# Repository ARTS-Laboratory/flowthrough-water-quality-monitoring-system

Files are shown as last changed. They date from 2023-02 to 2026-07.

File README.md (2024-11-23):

# Flowthrough Water Quality Monitoring System

This system monitors water quality by measuring conductivity, pH, and temperature, ensuring continuous operation with minimal maintenance. Moreover, versions of this system enable the use of time-domain nuclear magnetic resonance to be performed in situ. It features a robust construction that protects electrical components from environmental damage, supports an adequate flow rate for in situ water sampling, and enables data transmission to a server for analysis.

<p align="center">
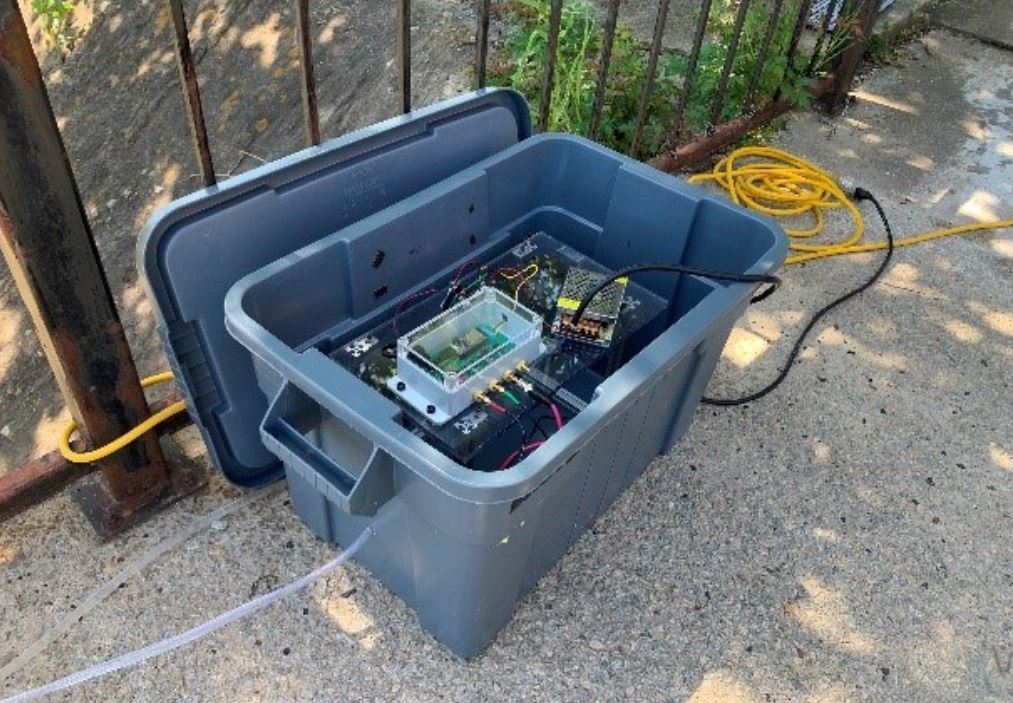
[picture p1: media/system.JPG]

</p>
<p align="center">
Figure 1: flow-through water quality monitoring deployed at USC to monitor water quality in the Rocky Branch in Columbia South Carolina.
</p>

## System Development
Contains the hardware and software developed for the project. 

## Licensing and Citation

This work is licensed under a Creative Commons Attribution-ShareAlike 4.0 International License [cc-by-sa 4.0].



Cite this as: 

@Misc{ARTSLabFlowthroughWaterQuality,    
  author = {ARTS-Lab},  
  howpublished = {GitHub},  
  title  = {Flowthrough Water Quality Monitoring System},   
  groups = {ARTS-Lab},    
  url    = {https://github.com/ARTS-Laboratory/flowthrough-water-quality-monitoring-system},   
}

<p align="center">
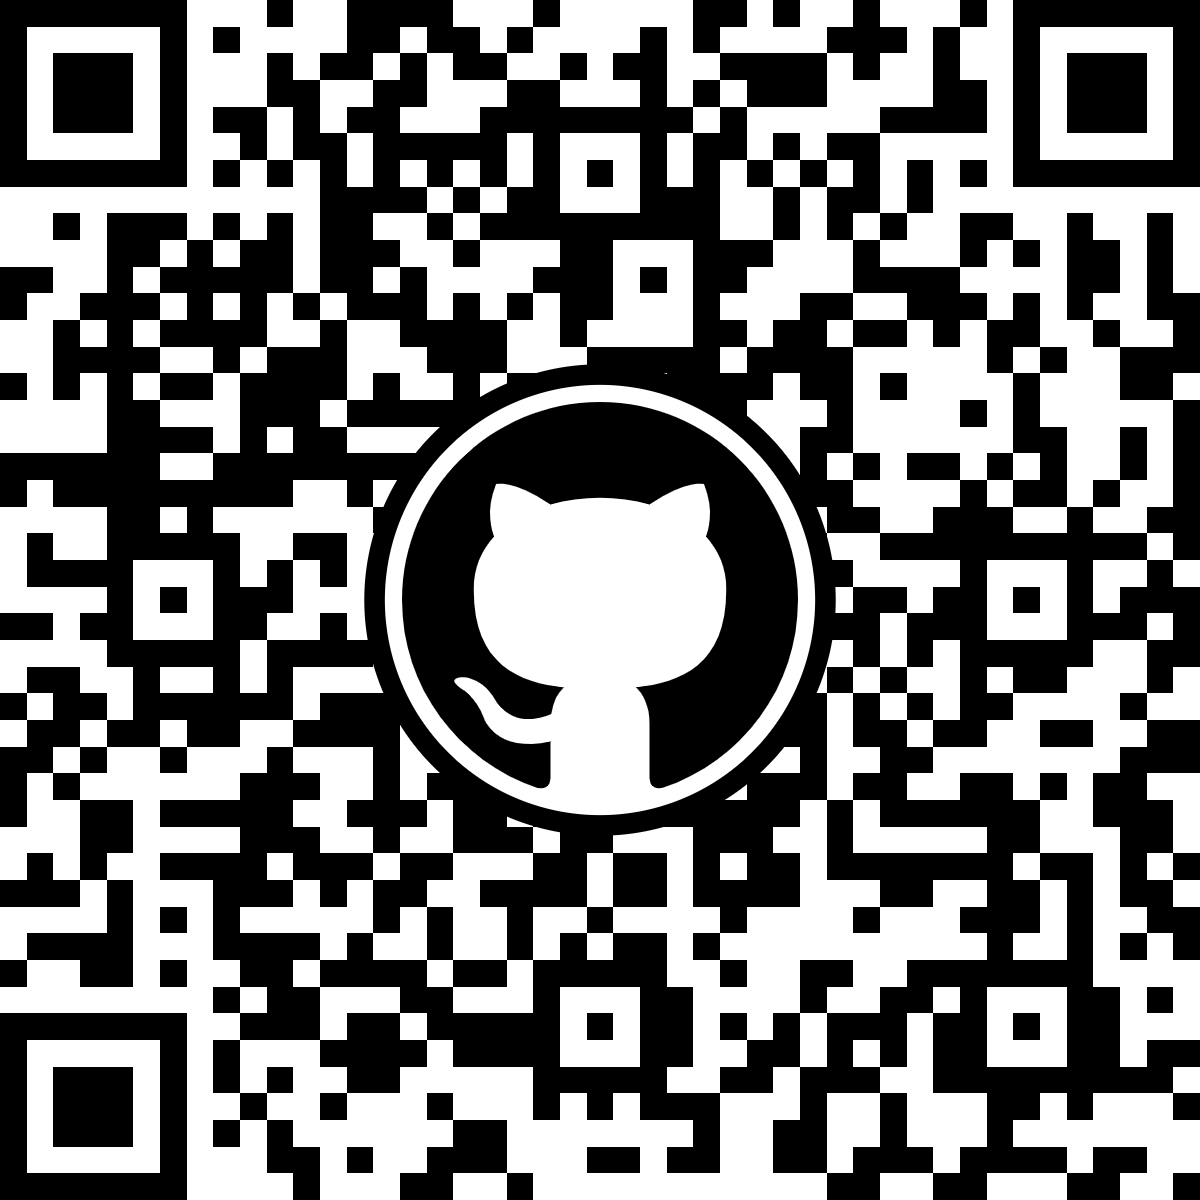
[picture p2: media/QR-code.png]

</p>
<p align="center">
QR code for repo.
</p>

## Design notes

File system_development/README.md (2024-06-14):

# System Development
Variations of the flow through the water quality system are being developed. Named after lakes in South Carolina 

## Keowee
A flow-through water quality monitoring system that measures PH, TDS, water temperature, and ambient temperature.

## Moultrie
A flow-through water quality monitoring system that integrates nuclear magnetic resonance monitoring and measures PH, TDS, water temperature, and ambient temperature.

## Marion
A prototype project beginning work in May of 2024 to combine a flowthrough NMR, a water quality, and a water height monitoring system.

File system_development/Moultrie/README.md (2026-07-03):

# Moultrie
A flow-through water quality monitoring system that integrated nuclear magnetic resonance monitoring as well as measuring PH, TDS, Water Temperature, and ambient Temperature.

## V0.1.0
An initial senior design project undertaken at USC that laid out initial system aspects. 

## V0.2.0
A senior Design projecc form teh spring-fall of 2025.

## V0.3.0 
A version further developed from the Senior Design project with simplified manufacturability and newer magnets.

## V0.3.1 
A cleaned up verion of V0.3.0 with the extra CAD files removed.

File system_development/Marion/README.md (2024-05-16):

#Files for use with the Prototype-24 project

##PCB Files
Kicad files as well as general information about the custom PCB's used with the water height monitoring and pumping system system.

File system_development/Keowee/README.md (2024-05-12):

# Keowee
A flow-through water quality monitoring system that measures PH, TDS, Water Temperature, and ambient Temperature.

## V0.1
1. An initial senior design project undertaken at USC that laid out initial system aspects. 

## V0.2
1. Measures PH, TDS, Water Temperature, and ambient Temperature.
2. Saves the Data collected on an SD card.
3. Using RTC to control and display the sampling time.
4. Using a relay to control the pumps.

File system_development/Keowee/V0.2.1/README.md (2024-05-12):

# V0.2
Measures PH, TDS, Water Temperature, and ambient Temperature and saves Saves the Data collected on an SD card.

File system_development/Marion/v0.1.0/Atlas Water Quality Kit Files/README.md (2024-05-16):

#Files for use with the Prototype-24 project and the Atlas Scientific Wifi Hydroponics 2.0 kit which we are using

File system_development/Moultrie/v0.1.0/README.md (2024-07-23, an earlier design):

# V0.1

Hello! Hopefully the work I did here was somewhat helpful. If you have questions about any of the physical structure or the Arduino relay system, please feel free to contact me at the following:

bmontroy25@governors.school (will work until the end of may, 2025)
braedenmontroy1@gmail.com (will always work)
228-382-8652 (quickest answer)

Hey, this is Ali. I continued to work on the water sensor array after Braeden left. If you have any questions about that array you can contact me at aliwallam16@gmail.com

# Pumps
The pumps we are using are 12V Grothen pumps. You'll need about 2 amps to run both of them at full power at the same time.
(https://www.amazon.com/dp/B0863TCH65)

# Relay
I've left a picture of the relay labelled in the same folder as this. It should have everything you need to get this going. Currently, the system works by powering the pumps whenever the D13 on the Arduino is on. As I was leaving, we were working on making this output a switch toggle.

<p align="center">
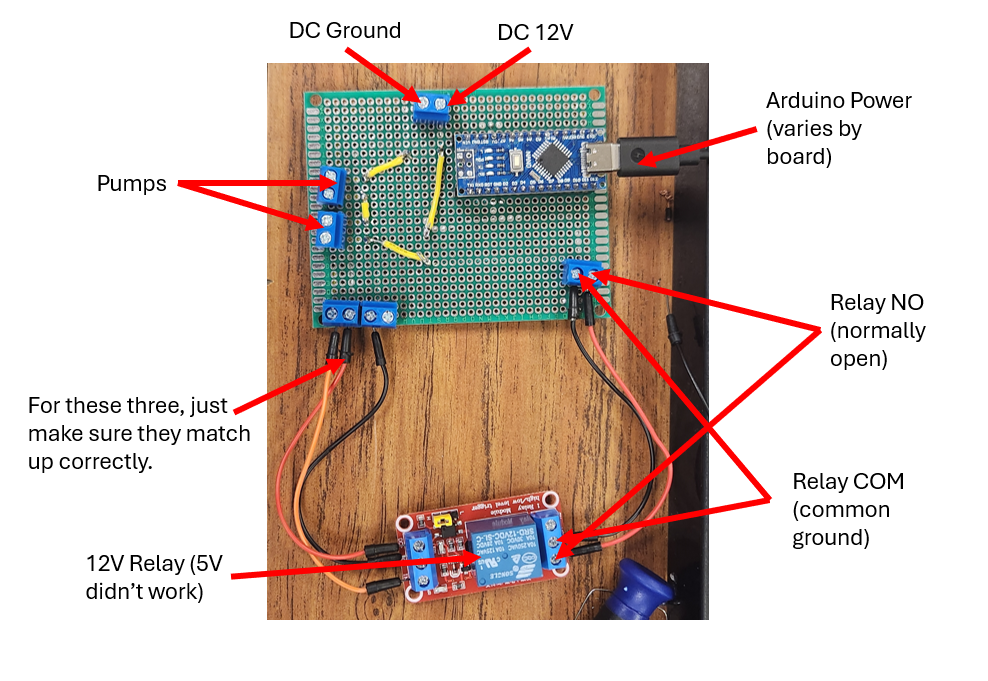
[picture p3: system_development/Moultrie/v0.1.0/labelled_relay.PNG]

</p>
<p align="center">

# Structure
The structure is currently made from 8020 and a sheet of what I think is Delrin. It doesn't fit in the box completely, as it needs about an inch to be chopped off the height in order to fit correctly, but all of the components fit inside of it. You can find CAD for this in the CAD folder in this directory. The next steps in terms of structure are to lower the right (or left) side to compensate for the PXIe, move all of the pumps to one side, use plastic screws and put the magnet on the other side, and make the connection between the pumps and the tubing and the sensor array watertight so water can actually run through the system.

# Water Sensor Array
Kit being used: https://atlas-scientific.com/kits/wi-fi-hydroponics-kit/

The array is now wired up to an SD card module as follows:
VCC (SD Card Module) to 3V (ESP32)
GND (SD Card Module) to GND (ESP32)
CS (SD Card Module) to GPIO 27 (ESP32)
MOSI (SD Card Module) to MOSI (ESP32)
MISO (SD Card Module) to MISO (ESP32)
SCK (SD Card Module) to SCK (ESP32)

The sensors themselves can take data and the code HFOIFHIOHFOIWHOW is set up to save the data to an sd card, they just need to be calibrated correctly to take data. The pH sensor currently connected to the array may not work together as it was not kept in the storage solution.

The kit is also connected to a TDS meter from keystudio: https://wiki.keyestudio.com/KS0429_keyestudio_TDS_Meter_V1.0

If you encounter issues they are likely power issues, in which case I would recommend adding a battery and a voltage regulator to the circuit.

<p align="center">
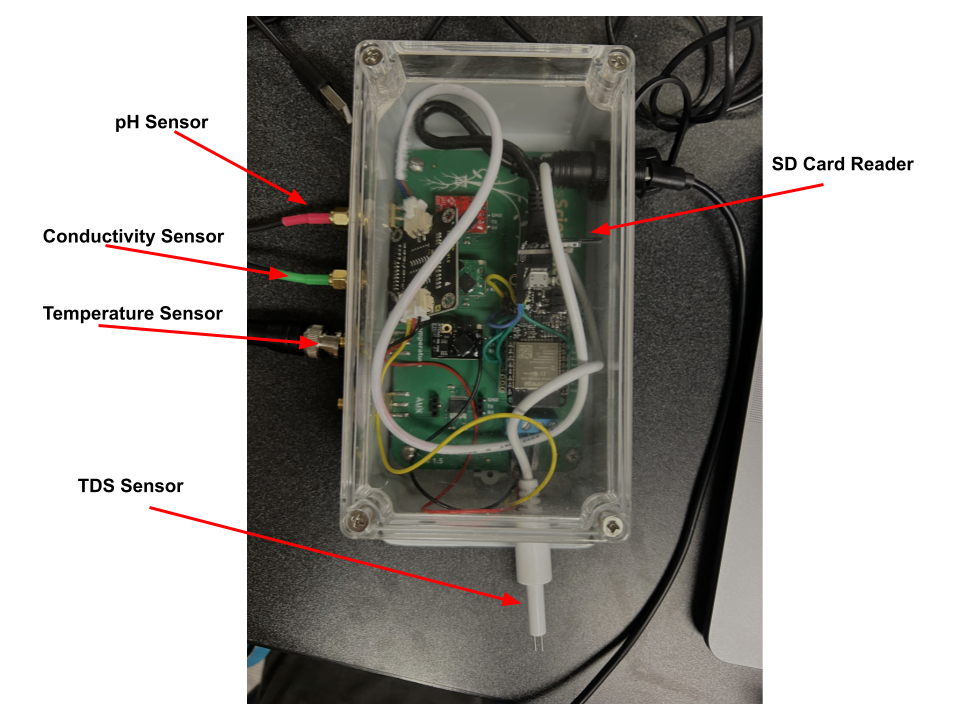
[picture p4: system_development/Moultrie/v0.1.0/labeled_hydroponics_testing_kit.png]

</p>
<p align="center">

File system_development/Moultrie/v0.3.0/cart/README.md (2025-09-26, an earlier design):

# Cart Design for the Moultrie V0.3
A fart for moving the flow-through water quality monitoring system that integrated nuclear magnetic resonance monitoring.

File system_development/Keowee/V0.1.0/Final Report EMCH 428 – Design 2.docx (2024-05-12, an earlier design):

In Situ Water Quality Measurement System

Abdullah Alghamdi, Carter hoyle, Michael Bertram, Grayson mobley

Final Report | EMCH 428 – Design 2

April 24, 2023

Department of Mechanical Engineering | University of South Carolina: Columbia, SC

Industry Sponsor: Dr. Austin Downey | The ARTS Laboratory

2. Table of Contents

Cover Page: 1

Table of Contents: 2

Executive Summary: 3-4

Background: 7

Customer Needs: 8-15

Project Specifications: 16-21

Functional Concepts: 22-31

Concept Selection: 33-35

Product Architecture: 36-39

Engineering Analysis: 40-50

Manufacturability: 51-56

Product Cost/ Economic Analysis: 58-62

Testing: 63-67

Final Design: 68

Conclusions: 69-71

Appendix: 72-73

3. Executive Summary

Dr. Austin Downey is a Professor at the University of South Carolina, and he oversees the Adaptive Real-Time Systems (ARTS) Laboratory that specializes in developing tools for systems that can adapt to the environment in real time. They want a product that does that can measure conductivity, pH, and temperature of water, provide adequate flow for fresh sampling, keep electrical components safe from water damage/heating damage, and will be able to transmit data to a server so they can have a device that can be compatible with the NMR.

The needs of Dr. Downey were determined by the project scope which gives a description of what the project entails and its deliverables, and the various project meetings that were held with the project sponsor, and after detailed analysis, it was determined that having sensors that can measure pH, measure conductivity, measure temperature, ease of manufacturability, keeping electrical components dry, and withstand various weather conditions were critical to satisfying those needs. It was furthermore determined that a product to satisfy their requirements would need to measure fresh water’s conductivity, temperature, and pH value. The key product specifications are running without maintenance for 2- 6 days, average power consumption around 6.5 Watts, and flow rate to be around 11.36 liters per minute. It was thus determined that the product mission should be: The ARTS-Lab at the University of South Carolina needs a device that can measure conductivity, pH, and temperature of water, provide adequate flow for fresh sampling, keep electrical components safe from water damage/heating damage, and will be able to transmit data to a server.

Given the above requirements, multiple concepts were researched and considered, as described in this report. The ultimate concept selected to best satisfy Dr. Downey’s needs was a design that includes the out of water, series flow. The concept was considered the best when scored against other ideas for its simplicity and ability to transmit data with low energy consumption. The product architecture concerning this concept outlined the interactions between the sampling water, power source, microcontrollers and the data transmitted to the cloud.

Circuitry, temperature regulation, pressure, and power regulation are critical to functionality, and detailed engineering analyses are provided, demonstrating how pressure change, current usage, and temperature variation were modeled, under peak outdoor operating conditions. The design was optimized for clearer sensor readings, lower temperature gradients, and as-designed power constraints as a result.

Because parameters of component selection (Power supply), protection (Power Supply), stability (Hydronics sensors), and symmetry (PVC piping) are high priorities for production of the product, the design was optimized for these parameters as well, which consisted of comparing 50-Watt and 60-Watt power supplies, designing a 3D printed cover for the power supply, using three PVC tees and cable glands to secure the hydronics sensors, and cutting the PVC pipe into 4 equal sections.

The prototype was tested by doing flow rate and circuit analysis, as well as an endurance test condition ranging from indoor, protected conditions to exposed, outdoor operating conditions.

Economic analysis of the scope of expenses associated with development of the prototype indicates that, for a $652.91 investment (including labor), Dr. Downey will recover costs within 3 months.

This design was determined not to be a viable start for water quality measurement. The design performed within the specifications that were listed, but in testing, the effectiveness of the water quality measurement was lackluster. The design has room for many new specifications for the design to become viable in the future. It is suggested that the prototype undergoes a major redesign with the knowledge learned from the tested components and their orientation.

4. Background

The University of South Carolina Adaptive Real-Time Systems (ARTS) Lab specializes in developing tools for systems that can adapt to the environment in real time. They have done work on machine learning, sensor packaging, autonomous and embedded systems, real time control, and artificial intelligence. Their goal is to build interdisciplinary systems that can be applied to various mechanical, aerospace, computer, and civil infrastructures.

The purpose of this project is to develop a system that hosts a suite of sensors for collecting, processing, and transmitting data remotely to a central server. The system will initially measure conductivity, pH, and temperature and integrate a custom NMR sensor developed by the ARTS-s Lab. The system would be expandable while providing power management and cooling. In-depth thermal models of the system will need to be developed for analysis. The goal of the project is the development of a flow-through water quality measurement system.

5. Customer Needs

5.1 Introduction

The project is an In-Situ Water Quality Measurement System, and the sponsor is The Adaptive Real-Time Systems Laboratory (ARTS-Lab) at the University of South Carolina. The project contact is Austin Downey, Assistant Professor. The design is a concept that can transmit collected data from sensors to a remote server using CAD files and source code. Using an Atlas Wi-Fi sensor which has a temperature, conductivity, and pH probes, the design will collect readings for pH value, conductivity, and temperature readings of flowing water, because the goal of the project is to development of a flow-through water quality measurement system. The readings will be collected from the creek water located behind the 300 Main St. building. This design incorporates pumps, plastic tubing, and PVC pipes to control the water going into the system. The stake holders are Dr. Downey and graduate students working in the ARTS Lab because they will be using the product and readings to benefit the NMR sensor.

5.2 Methodology

To find the needs necessary for the project, we used two sources. Those being the project scope which gives a description of what the project entails and its deliverables, and the multiple project meetings that were held with the project sponsor. From the scope we were able to create needs that met the requirements for what was stated, such as being able to measure pH, conductivity, and temperature of the water. The project sponsor meetings also gave insight as to certain conditions that are necessary for the project such as being able to run for a week without maintenance and being compatible with the NMR box. There is a graduate student in the ARTS Lab working on a similar project, but his system is much different. He gave some recommendations but overall wasn’t helpful with developing needs for this system.

From the information above, a list of needs is produced:

- Run for a week w/o maintenance.
- Last for months on end.
- Fit into the ditch behind 300 Main Bldg.
- Remain secured to the base of the trench to prevent drifting.
- Cost effective.
- Have a cooling system (ex. water cooling).
- Safely run when unsupervised.
- Be able to measure conductivity, pH, and temperature of water.
- Be compatible with the NMR Box.
- Be easy to understand for use.
- Be able to have water at room temperature.
- Collect data from sensor.
- Be able to transmit data to a server.
- Be able to work in water.
- Keep electrical components safe from water damage/heating damage.
- Show thermal modules.
- Be able to adjust the power of sensors and pumps.
- Be able to work in certain temperatures.
- Be expandable, so more work can be done on it.
- Be able to be removed (for maintenance when necessary).
- Be easy to install.
- Differentiate between room temperature water and other forms of water (pH, temperature, conductivity)
- Check water in real time.
- Be able to differentiate bacteria in water.
- Measure flow rate.
- Have separate sensors to give feedback on the design, i.e., thermometers on important components.
- Have no negative effects on the water it is measuring.

5.3 Interpretation of Needs

The product needs to be able to run for a period without maintenance, as well as last for a few months. This is important because the product must run without the engineers constantly around it.

The product needs to be small enough to fit into the ditch behind 300 Main St. building but also big enough to where it won’t float downstream.

The product needs to fit the budget given by the sponsor, which means each part must be carefully selected and the price of each part must be taken into consideration.

The product needs to have a cooling system since the product will be outside in the heat or in the sunshine. Also, the product will be in an enclosed box so the internal temperatures will rise.

When the product is unsupervised, it must run safely without products overheating and blowing up. Overheating components will cause an unsafe environment, which is unacceptable because it could hurt someone passing by or cause environmental damage.

The product must measure the pH, temperature, and conductivity of the flowing water. This means the product must incorporate three sensors to measure these values.

The product needs to be compatible with the NMR box provided by the sponsor. This means the product must either have the NMR box incorporated into the design or the readings collected from the product must be able to transmit to the NMR box.

The product must be easy to use. This means any engineer from the ARTS lab can use our product to collect data without confusion or problems with using the product.

The product needs to have a component consisting of water at room temperature to use as a base for the temperature, pH, and conductivity data collected.

The product must collect data from the sensors and then transmit that data to a server. This means that the sensors that are selected must work properly, and the design needs to have a device that can send the data collected to either a computer or phone.

The product must be able to work in water. The product isn’t going to be submerged in water, but it will be partially in water, so it needs to be either sealed or water resistant, so water doesn’t get inside of the product and get the electrical components wet.

The product needs to show thermal modules, meaning the user can see which parts or components are heating up so appropriate changes can be made to ensure the correct temperature of said components.

The product needs to be able to adjust the power of the sensors and pumps, because the sensor and pump require different power inputs. This can be achieved by using a voltage regulator.

The product must work in various outside conditions such as in the heat, the cold, and in humid environments. This is important because the product must run for multiple weeks and in South Carolina the weather can drastically change in a matter of a few weeks.

The product needs to be expandable so future work can be done on it, be able to be removed, and be able to be easily installed. This means the design will incorporate a removable frame consisting of the different components inside of the product. This frame can’t be mounted to the box but also needs to be fitted to the box, so the frame isn’t moving inside of the box.

The product needs to check water in real time which means that the sensors need to transmit data as soon as the water passes the sensors, then transmit the data immediately.

The Product needs to determine if there are bacteria in water. This is done using conductivity probes. The more polluted the water is, the higher the conductivity level will be.

The product needs to measure the flow rate of the water in the system. This is important because if the flow rate is too small then the sensors won’t be getting new water to test, and if the flow rate is too high then the tubing can burst causing the inside to get wet.

The product needs to have separate sensors to provide feedback on the design. This can consist of thermoset sensors to tell which components are getting hot and overheating.

Lastly, the product needs to have no negative effects on the water it is collecting because after the water is sampled, it will go back out of the creek. This is achieved by using electricity from and outlet to power the product. There can’t be any gases or particles from the product contaminating the water.

5.4 Prioritization of Needs

There were originally 27 customer needs produced after discussing with the sponsor and using the project scope. This is way too many needs to create a product, so a voting process was created to eliminate unnecessary needs and to find the most important needs to include in the product mission statement. The voting process started by creating an excel sheet with the original 27 needs and then splitting them into 3 categories for round 1 of voting. Each team member ranked what is believed to be the most important needs out of each category on a scale from low to high. For the first category, each member was allotted a total of 21 points, and the 21 points were distributed based on the importance of needs in that section. For example, the most important need would be given a score of 1 and the least important would be around 10. For the second category of round 1, each team member was allotted 66 points to distribute, and in the third category each team member was allotted 55 points to distribute. After the team finished voting, the scores were added up for each need and given a rank based on how low the total score was. It's like golf, the lowest score wins.

Table 5.1: Round 1 of Voting on Needs.

Round One
Needs to: | Grayson | Carter | Abdullah | Michael | Total Score | Overall Rank
Run for a month w/o maintenance. | 2 | 2 | 6 | 4 | 14 | 3
Last for months on end. | 5 | 6 | 5 | 5 | 21 | 6
Fit into the ditch behind 300 Main Bldg. | 6 | 5 | 3 | 3 | 17 | 5
Be cost effective. | 4 | 4 | 2 | 6 | 16 | 4
Have a cooling system | 1 | 3 | 1 | 2 | 7 | 1
Safely run when unsupervised. | 3 | 1 | 4 | 1 | 9 | 2
Be able to measure conductivity, pH, and temperature of water. | 2 | 1 | 1 | 2 | 6 | 1
Be compatible with the NMR Box. | 1 | 2 | 2 | 1 | 6 | 2
Be easy to understand for use. | 9 | 8 | 7 | 4 | 28 | 7
Be able to have water at room temperature. | 8 | 9 | 8 | 10 | 35 | 10
Collect data from sensor. | 7 | 3 | 4 | 9 | 23 | 6
Be able to transmit data to a server. | 4 | 5 | 5 | 5 | 19 | 4
Be able to work in water (water resistant). | 3 | 10 | 3 | 7 | 23 | 5
Show thermal modules. | 10 | 6 | 9 | 6 | 31 | 9
Be able to adjust the power of sensor. | 5 | 7 | 10 | 8 | 30 | 8
Be able to work in certain temperatures (heat, humidity, cold). | 6 | 4 | 6 | 3 | 19 | 3
Be expandable, so more work can be done on it. | 11 | 11 | 11 | 11 | 44 | 11
Be able to be removed. | 7 | 8 | 7 | 7 | 29 | 8
Be easy to install. | 6 | 7 | 6 | 10 | 29 | 7
Differentiate between room temperature water and other forms of water (pH, temperature, conductivity) | 8 | 5 | 8 | 5 | 26 | 6
Check water in real time. | 3 | 6 | 5 | 1 | 15 | 4
Be able to differentiate bacteria in water. | 10 | 9 | 9 | 9 | 37 | 10
Remain secured to the base of the trench to prevent drifting. | 1 | 4 | 4 | 2 | 11 | 3
Keep electrical components safe from water damage/heating damage. | 4 | 2 | 2 | 3 | 11 | 2
Measure flow rate. | 2 | 1 | 1 | 6 | 10 | 1
Separate sensors to give feedback on the design, i.e., thermometers on important components. | 5 | 3 | 3 | 8 | 19 | 5
Have no negative effects on the water it is measuring. | 9 | 10 | 10 | 4 | 33 | 9

Round 2 consisted of the top 4 needs of each category from round 1 which resulted in 12 total needs. These top 4 needs are considered critical to quality (CTQ’s). Round 2 was not split into different sections, just one big section. The voting process changed a little bit for this round. Each team member voted on a scale of 1-12 with 1 being the most important and 12 being the least important, instead of each member given a total amount of points to distribute. After every team member voted, the six lowest ranked needs became the most important CTQ’s, the mission statement will consist of these top six CTQ’s. It was determined that focusing on a maximum of 6 CTQ’s will improve the design concept without having to worry about focusing on needs that the sponsor thinks will be irrelevant.

Table 5.2: Round 2 of Voting on Needs.

Round Two
Needs to: | Grayson | Carter | Abdullah | Michael | Total Score | Overall Rank
Have a cooling system (ex. water cooling). | 1 | 10 | 8 | 9 | 28 | 8
Safely run when unsupervised. | 6 | 9 | 7 | 7 | 29 | 9
Run for a month w/o maintenance. | 4 | 7 | 9 | 8 | 28 | 7
Be cost effective. | 11 | 12 | 10 | 12 | 45 | 12
Be able to measure conductivity, pH, and temperature of water. | 2 | 1 | 1 | 1 | 5 | 1
Be compatible with the NMR Box. | 7 | 5 | 6 | 4 | 22 | 5
Be able to work in certain temperatures (heat, humidity, cold). | 8 | 8 | 11 | 10 | 37 | 10
Be able to transmit data to a server. | 12 | 2 | 4 | 2 | 20 | 4
Measure flow rate | 3 | 3 | 2 | 3 | 11 | 2
Keep electrical components safe from water damage/heating damage | 5 | 4 | 3 | 6 | 18 | 3
Remain secured to the base of the trench to prevent drifting | 9 | 11 | 12 | 11 | 43 | 11
Check water in real time. | 10 | 6 | 5 | 5 | 26 | 6

The top 6 design needs that are critical to quality are:

1. Be able to measure conductivity, pH, and temperature of water. (Clear 1st)
2. Measure flow rate. (Clear 2nd)
3. Keep electrical components safe from water damage/heating damage.
4. Be able to transmit data to a server.
5. Be compatible with the NMR Box.
6. Check water in real time.

5.5 Product Mission Statement

Using the top final needs that are critical to quality determined from the voting processes, a mission statement was created: The ARTS-Lab at the University of South Carolina needs a device that can measure conductivity, pH, and temperature of water, will measure flow rate, will keep electrical components safe from water damage/heating damage, and will be able to transmit data to a server.

6. Project Specifications

6.1 Introduction

The purpose of this report is to identify metrics for the customer requirements and to create target specifications using a House of Quality approach. After the metric table was created, a House of Equality table was created. This table compares the customer requirements with the engineering characteristics, to create a ranking of the engineering characteristics. Lastly, a target/fallback table was created. References were used to determine the target specifications and the fallback specifications for each. Key outcomes of this chapter are defining the target and fallback values of necessary metrics, determining the critical engineering characteristics to focus on, and which metrics will be challenging to satisfy.

6.2 Methodology

Table 6.1: Customer Requirements and Metrics for In-Situ Water Testing Suite

Sponsor Requirements | Metrics | Units
Compare conductivity to NMR | Measures conductivity | [EC]
Compare pH to NMR | Measures pH | None
Track natural water temperature | Measures temperature | [C]
Measures flow rate | Measures flow rate | [Liter/Min]
Electrical components must stay dry | Electrical components must stay dry | [Boolean]
Electrical components will remain functional in all weather conditions | Temperature regulation near operating temperature of electrical component | [C]
The suite will supply water flow compatible with the NMR Box. | Fluid temperature change over time | [C/Min]
The suite will transmit data wirelessly in real time | Data sets per unit time | [Data Sets/Min]
The suite will require minimal maintenance | Time without maintenance | [Days]
The suit must be able to be carried with ease. | Portability | [Lb]
The suite must have enough power supplied for the pumps and sensors to work | Average Power consumption | [Watts]

The sponsor requirements list in table 6.1 were produced from the voting system in chapter 5. Also, a few more were added in this section based on suggestions from the faculty mentor, such as portability and average power consumption. This design is primarily about supporting the Nuclear Magnetic Resonance (NMR) box. Primary needs in the design are regulating fluid properties for use in NMR. In the process of regulating the fluid, there are many opportunities to collect more data on the flowing water. The fluid properties that are to be measured reflect the customer’s criteria for satisfaction.

Data collection includes conductivity, temperature, flow rate, and pH. Temperature and flow rate are both properties that are important for the NMR and general regulation of the design. pH and conductivity give typical, valuable information regarding the water in the reservoir.

To make the data collection accessible and useful for the customer, the data was recorded electronically. Rather than physically checking the data at the site of the product, there should be capability to send data wirelessly for viewing. Wireless data viewing, as well as automatic compilation of data, requires electrical components, which must be kept dry and properly sustained for the duration of its use, hence the requirement for steady temperature of components.

6.3 Needs Metrics Matrix (or House of Quality)

The House of Quality begins with taking the customer requirements stated in the Specifications Metrices. Engineering characteristics were then formed based on what is necessary for all the requirements to produce a satisfactory product. This led to the characteristics of Power input, Temperature Regulation, Fluid Pressure, Ease of Access, Height, Length, Width, Product Stability, and Cost to Manufacture. Appropriate units were given based on said characteristics, and then an improvement direction was given based on whether increase or decrease a certain characteristic would improve to the product. Each Customer Requirement was then given an Importance Weight Factor for the entire project. Numerical values were used from 1-5 with 1 being least important and 5 being the most. Each requirement would then correlate to specific engineering factors that they would affect, and then receive a numerical value from 1 to 9, with 1 representing slight contribution, 3 being moderate, and 9 being the strongest contribution. The weight factor would then be multiplied in each row to the contribution number and added altogether in the column. These columns would be added all together to form a raw score, with a weight percentage given using each column’s sum divided by the raw score multiplied by 100. Unlike how the needs were ranked in the voting process in chapter 5, the ranking in the House of Quality matrix were based on how high the score is. The more points means that it is more impactful to product quality and customer satisfaction.

Table 6.2: House of Quality Matrix

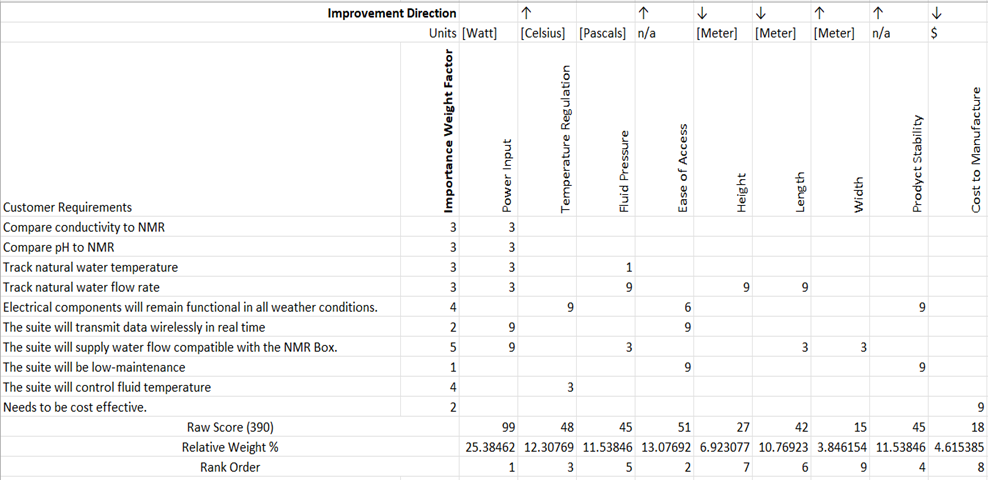
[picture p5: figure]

In observation, the requirement Track natural water flow rate and the suite will supply water flow compatible with the NMR box have the highest number of matrices, those being power input, fluid pressure, height, length, and width. Power Input will have a strong focus because of all the different processes it needs to power, including all the different quantities measured in the water (temperature, pH, conductivity).

6.4 Target and Fallback Specifications

After team members discussed each need target, which are the ideal goal that could be achieved. The second phase of searching and looking to the probability of the ranges to achieve this target.

The target values were obtained after meeting with the project sponsor, Dr. Downy, and talking about the needs report to identify the method of how the system will collect the data needed. To know the targets of this system, searching on the internet for systems and sensors that are already on the market to know the range of how these systems work.

The table below (Table 6.3) illustrates the targets for the metrics and the fallback values. Also, the reference number. As mentioned before. Similar systems properties like Arduino were valuable resources to identify the targets of this project.

Table 6.3: Target and fallback values for the metrics

Metrics | Units | Target Specification | Fall Back
Measures conductivity | [EC] | 750 | 500 - 1000
Measures pH | None | 7 | 6.5 - 7.5
Measures temperature | [C] | 22 | 21-23
Measures flow rate | [Liter/Min] | 11.36 | 7.75 - 15.14
Electrical components must stay dry | [Boolean] | True Positive | TP - TN
Temperature regulation near operating temperature of electrical component | [C] | 23 | 40 - 60
Fluid temperature change over time | [C/Min] | 5 | 20
Data sets per unit time | [Data Sets/Min] | 0.2 | 0.1
Time without maintenance | [Days] | 10 | 2 - 6
Portability | [Lb] | 40 | 25 - 55
Average Power consumption | [Watts] | 6.5 | 5.0 - 80

6.5 Conclusions

Based on table 6.2, the critical engineering characteristics of the design are the power input, ease of access, temperature regulation, product stability, and fluid pressure. The height, width, and length of the product aren't too impactful on the design and the sponsor supplied a container for the product that had a set height, width, and length. Also, the cost of the design meets the budget because most of the materials were supplied from the ARTS Lab.

The metrics that will be challenging to satisfy are temperature regulation near operating temperature of electrical components, and time without maintenance. The temperature of the electrical components will get hot while the product is running continuously and since the product will be outside and in an enclosed container. Also, the time without maintenance will be challenging because the electrical components may overheat after a day of running which will require maintenance, and there isn't a design to keep the product from getting stolen when left without supervision.

7. Functional Concepts

7.1 Introduction

This report is meant to break down the design concepts of the product and to identify its functions. It will also cover several different ways that the needs of the product are satisfied, which will be evaluated in the next week to determine the viable options for the design. After the functional decomposition, a few design concepts will be reviewed as potential directions for our design to take.

7.2 Functional Decomposition

Functional decomposition is a process used to ideate design details. It begins by determining the functions that a product must entail to be considered satisfactory to a customer. These functions will be mapped in a diagram that tracks interactions between functions, like materials, energy, or data.

The functional diagram and functions are listed as follows:

- Measure pH of water sample
- Measure conductivity of water sample
- Measure temperature of water sample
- Measure flow rate
- Transmit data to a server
- Receive power
- Temperature adjustment
- Extracts water samples
- Receives user's input
- Stores/ejects sample

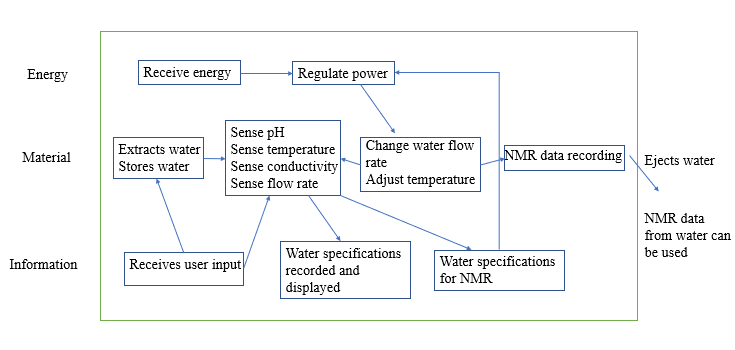
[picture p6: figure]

Figure 7.1- Functional Diagram

There are three flowing components that are important in the functional diagram to track: energy, material, and information. The energy in the product is related to the sensing functions as well as any functions that are required to do work of any kind. In the diagram, notice that energy is received, then regulated. No matter what, the energy in the system is regulated before it is utilized in other components. Power is going to be related to the water flow and to the heating and cooling of the water for the NMR box. The pH, temperature, conductivity, and flow rate sensing are all going to be derived from materials, or plainly the water flowing through the design. The NMR box will also be taking data from the material (water), and it will finally leave the sensing suite back to the reservoir or flowing stream. Information that the design obtains is specifications regarding the water flow. Notice that specifications regarding the NMR are fed back into the power regulation to change variables in the flow and temperature of the water.

Conclusively stated: the product needs to receive user’s input, intake and store flowing water, record data on the water, regulate the flow and temperature of the water, adjust the temperature, fill the NMR box adequately before it is returned to the reservoir, and eject the water back into the creek.

7.3 Concept Combination

A concept combination table (CCT) is a step in the concept generation process. Multiple functions that the intended system must follow will be in the top row of the table. Each function will then have its own column of different ways to achieve that function. CCT is useful because it helps generate a clear combination of elements for the design out of a long list of different options. The system must have a source of energy, a way to turn on the equipment, and receive the user’s input. It must also extract water from the creek and receive and send Values of ph., flow rate, conductivity, and temperature from the water samples. It must eject the sampled water back into the creek

Table 7.1: Concept Combination Table

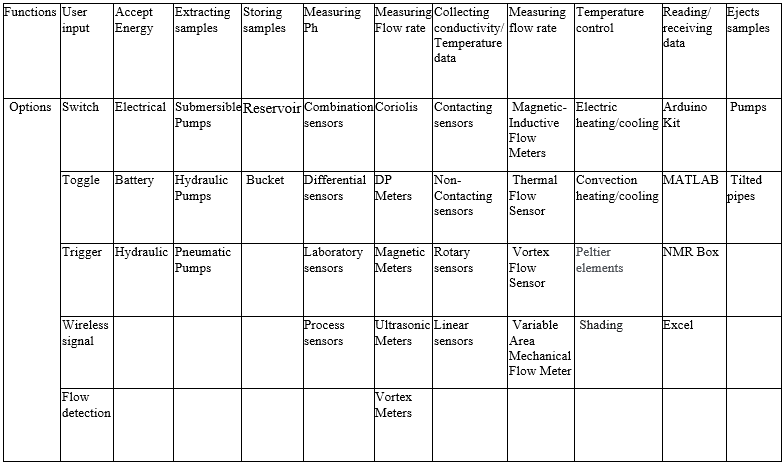
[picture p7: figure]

7.4 Concept Generation

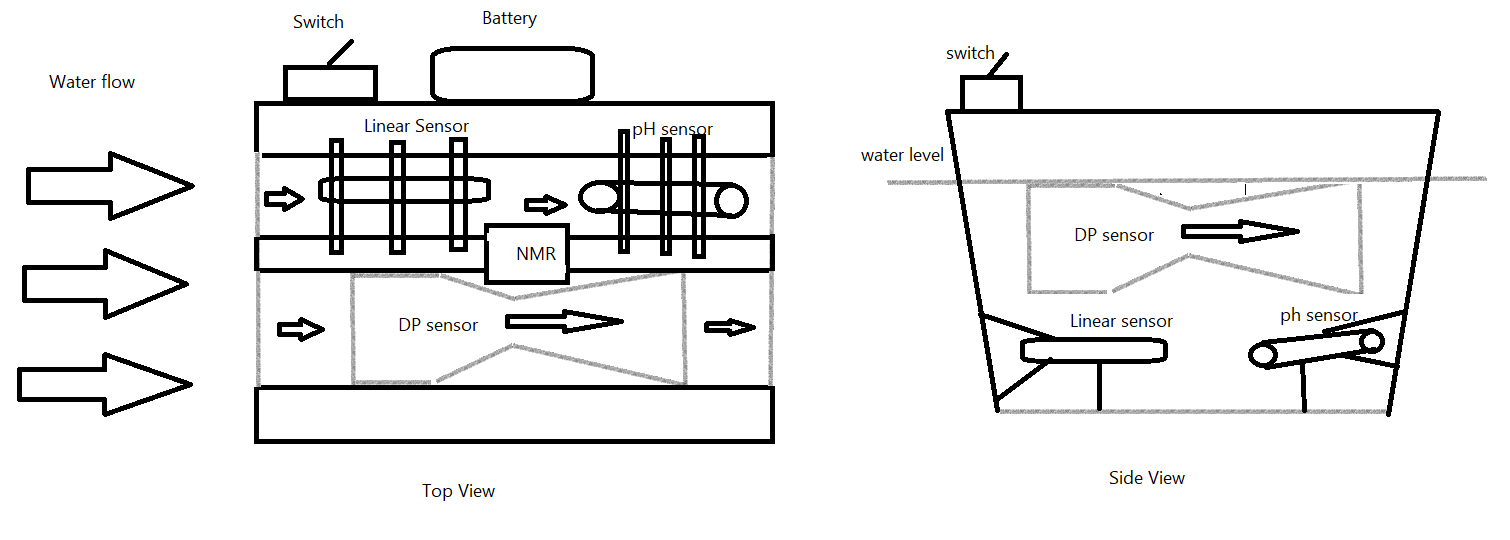
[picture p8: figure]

Figure 7.2 – Concept design

The design in figure 7.2 had the following concept combination: an on/off switch, a battery, a combination ph. sensor, differential pressure (DP) meter, linear sensor, shading from environment, and an NMR box. The system is split into two streams to make room for all three sensors. The sensors are powered from a battery attached to the outside and above the water flow to protect it from getting wet. The linear and ph. sensors will be submerged in the water but attached to the apparatus with multiple metal rods to ensure the sensors don’t break off. The use of a venturi tube design can measure flow rate. All the sensors will transfer the data collected to the NMR box which will then be transmitted to a server/ user interface.

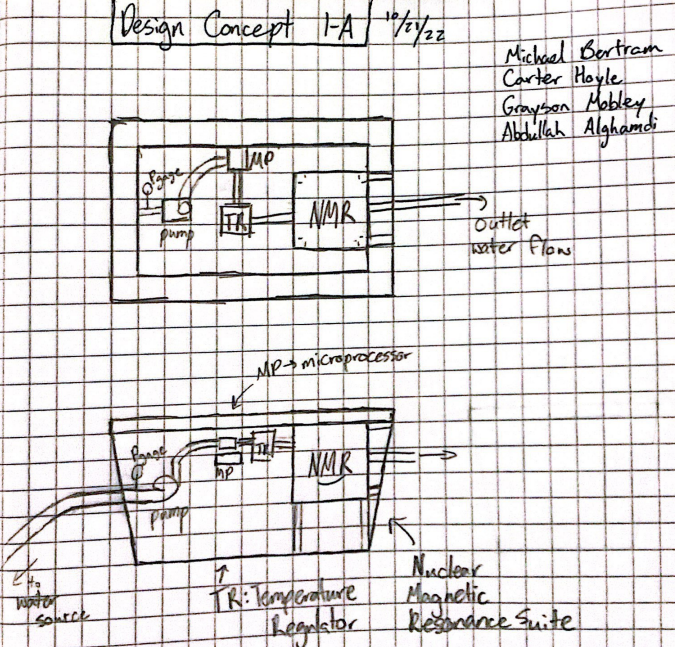
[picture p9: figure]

Figure 7.3 – Concept Design

Figure 7.3 features another design that uses a hydraulic pump and a water inlet line to bring pressurized water into the suite. A pressure gauge, sensing suite, temperature regulator, and the NMR box all receive and distribute water in that order at the same height from the water’s surface. A key difference in this design than to the one in figure two is that it is completely out of the water, and one of the needs that may be challenged is temperature control of both the electronics and of the water. Without being in flowing water, natural cooling won’t be able to contribute to the exterior of our design.

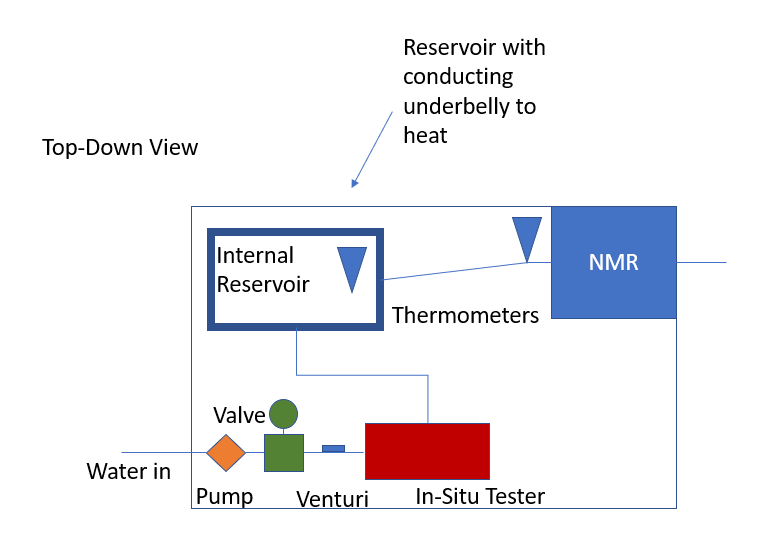
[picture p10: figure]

Figure 7.4 – Concept Design

Figure 7.4 is the third concept idealized. Key features to this design concept are a valve, internal water reservoir, and heating apparatus attached. The design of the reservoir makes heating incredibly simple to design, but likely difficult to keep consistent temperatures for NMR box intake. Power to the internal reservoir and therefore the heat added to the fluid would be dependent on one of two thermometers measuring the temperature of the water. The water also may not contain particles that are expected for the NMR box, because if they have different masses and aren’t in a constant state of flow, it’s possible for a residue buildup in the reservoir that could improperly affect results.

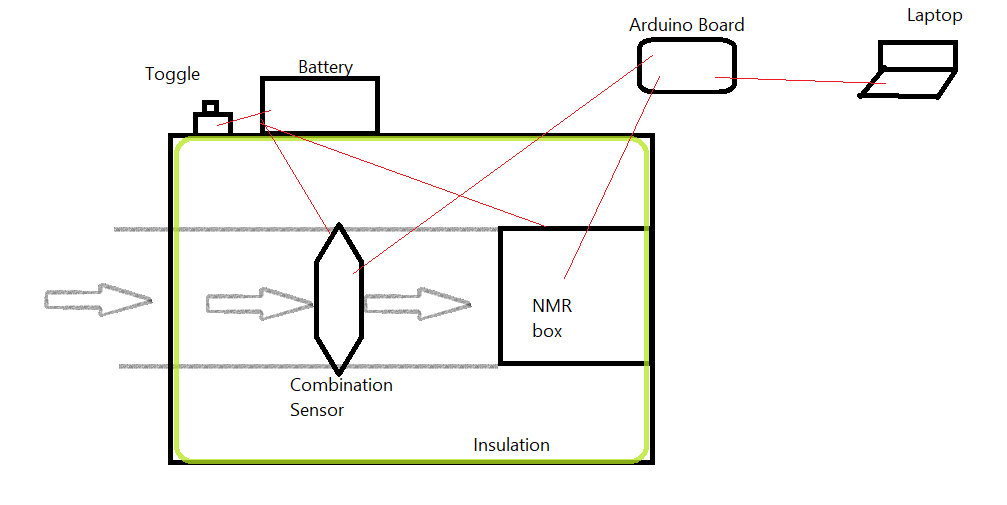
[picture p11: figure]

Figure 7.5 – Concept Design

The design in figure 7.5 consists of a toggle switch, a battery, a combination sensor, insulation, NMR box, Arduino board, and a laptop. The system will be powered by a battery with a toggle attached. The battery will power a combination of ph., temperature, and conductivity sensors all in one, as well as powering the NMR box. The sensors and NMR box are connected to an Arduino board configured to receive the data collected and then transmit the data to a nearby laptop or computer to display the data. The system will be in a plastic or metal box, and the box will be insulated for temperature control.

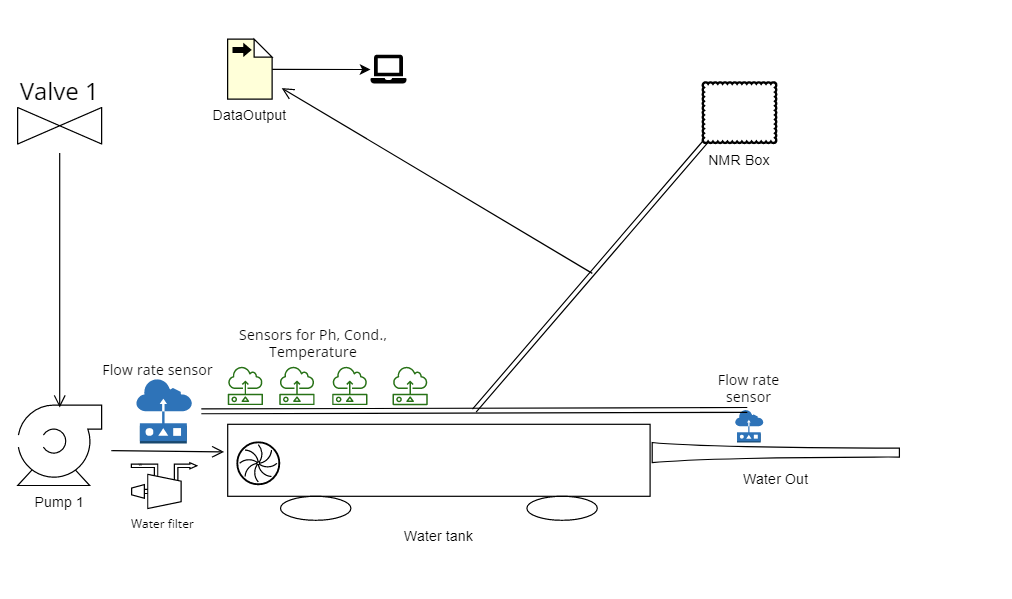
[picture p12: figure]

Figure 7.6 – Concept Design

The concept design in figure 7.6 contains a valve, a submersible pump and water tank prepared with suite of wireless sensors to measure the required properties. Such as Ph, conductivity, water temperature and flew rate in and out of the system. The water tank is equipped with a temperature controlling system as well as a water filter for keeping the samples flow clean. The system is connected to NMR Box and wirelessly sends data to be stored and viewed on a computer.

Figure 7.7 - Concept Design

The concept design in figure 7.7 is battery powered and uses a switch to execute overall functions. A water inlet for an external water source along with a pneumatic pump is used to bring water inside of a compartment. This inlet will have a flow rate sensor within and will be connected to the Arduino unit. Once in the compartment, a set of sensors will be used for the pH, conductivity, and the temperature of the external water. These sensors will also be connected to the Arduino unit. Above this Compartment is a second reservoir which will hold a certain amount of water. This reservoir will have electrical heating and cooling in order to regulate the water within to a certain temperature (this will most likely be room temperature). This reservoir of water will be used as a basis of comparison for the external water coming in, with its own set of Arduino sensors. A laptop will be connected to the Arduino unit showing all values of both compartments, as well as a separate display for the flow rate. The external water will then be transferred to the NMR box. Once its data has been collected, the NMR data will have its own display for information. The external water is then let out through an outlet in either a compartment attached, or a larger body of water.

7.5 Research Performed

The research performed was conducted on Google’s patent searching website, scholar.google.com. Some of the patents researched included key words like heating, cooling, flow, control, feedback, and water. We also researched current patents on nuclear magnetic resonance (NMR), as it is going to be related to details of the design. A venturi tube used for flow rate measurement was found using the key words differential pressure meter.

7.6 Conclusions

Some of the important factors in our concepts revolve around temperature control and the order of operations regarding the sensing and temperature regulation of the materials. Regarding order of operations, consideration must be paid to the customer’s requirements. When should the conductivity be sensed? When can the temperature be sensed, and where? Should there be more than one thermometer in the system? All of these questions will be taken into account in the future selection of concepts. The customer most primarily needs to collect data on the water and then make it compatible with the NMR box.

8. Concept Selection

8.1 Introduction

The aim of concept generation and selection is to develop several plausible solutions for the customer and evaluate them according to critical selection criteria to meet their needs. A selection matrix is used to screen these concepts and score them based on the selection criteria. The selection process involves a subjective ranking to determine the reference concept, and other concepts are rated as better, as good as, or worse than the reference concept. The grades are aggregated into net scores, which provide a more objective ranking of the concepts. This approach prioritizes customer needs and helps select the best option without bias.

8.2 Concept Screening

Six selection criteria are used to evaluate each concept: durability, power efficiency, component safety, cost-effectiveness, ease of cooling, and data availability. To create a rating table, a reference concept is chosen for comparison, and each subsequent concept is evaluated against the reference based on each criterion. The concept receives a “+” if it outperforms the reference, a “0” if it is equivalent, and a “-” if it is inferior. The total number of “+”, “0”, and “-” are tallied to calculate the net score, which is the difference between the total number of “+” and “-”. The ranking of the concepts is based on the net score, with the top-ranking design having the highest net score.

8.3 Concept Ranking

Table 8.1 – Concept Selection Matrix, round 1

Table 8.2 – Concept Selection Matrix, round 2

In the second round of concept selection, Concept B and the reservoir design were eliminated. Concept B's performance was unsatisfactory in terms of cost-effectiveness and data availability, while the reservoir concept had poor ratings in power efficiency, ease of cooling, and component safety. The remaining two concepts were compared against the reference concept using the same selection criteria. The Out of Water concept received a higher overall score, making it the top-ranked design.

8.4 Final Concept

The final concept chosen was the Out of Water, Series Flow design. This design utilizes an Atlas Scientific Hydroponics kit with probes attached to a 5mm (about 0.2 in) tube, regulated by a battery-powered pump. The design's key features include its simplicity, compatibility with NMR, and wireless data collection capabilities. However, there are challenges that need to be addressed, such as powering the pump, ensuring sustainability, and meeting the NMR box's water source criteria for sample testing. For the NMR box to function correctly, a static water source must be provided.

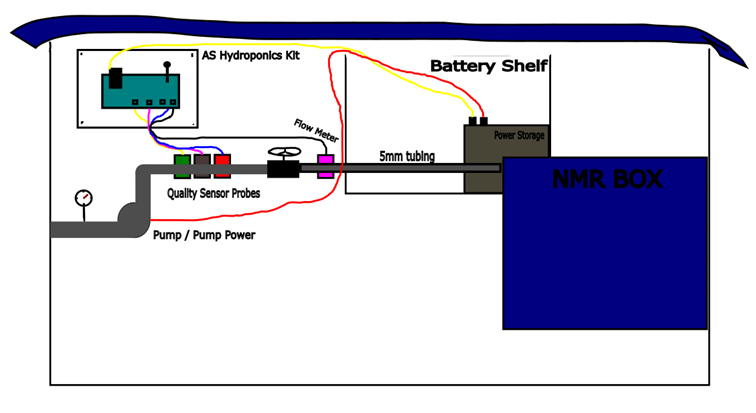
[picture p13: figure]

Figure 8.1 – Out of Water, Series Flow Concept

The selection of this concept has introduced new design criteria. The customer has requested a power profile of the design's components to make it self-sustaining. The pump and flow meter will need to work together to refill the NMR with fresh water after each data recording interval. This design was deemed the most suitable starting point for meeting the project's scope and delivering a product that meets the customer's needs.

9. Product Architecture

9.1 Introduction

Product architecture refers to the organization of a product's functional elements into physical building blocks, often achieved through clustering, as shown in Figure 1. Key considerations for making architecture decisions include the placement of elements relative to each other, which elements should be grouped together, and whether they should be integrated or modular. Figure 1 presents a modular approach to functional decomposition, with energy usage, data recording, and data sensing being the primary considerations for grouping the In Situ Water Quality System.

The main objective of the current product architecture is to quickly develop a prototype that can be used to study the power profile of the design. By having a functional design that can read assigned characteristics and utilize the NMR box, the foundation for a sustainable project is established. Once the prototype is constructed, the power consumption of each component can be analyzed to identify weak points in the design and areas where energy can be conserved or optimized for greater efficiency.

9.2 Product Layout

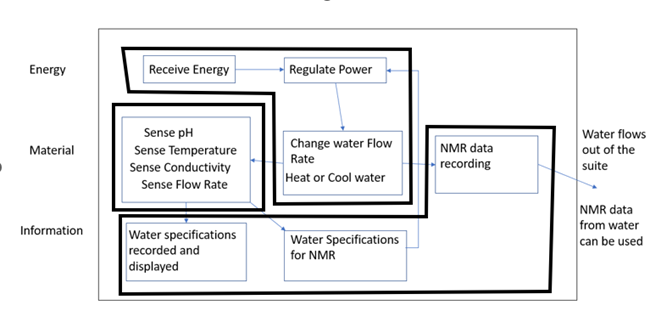
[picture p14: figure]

Figure 9.1: In Situ Water Quality System Function Decomposition

The functional decomposition diagram serves as the basis for our product layout. Three main sections for the functions, namely Energy, Material, and Information, are presented in Figure 1. Within these sections, the functions, which encompass the data being collected from the water, the suite's power source, and data recording, have been grouped. The sensing function of pH, temperature, conductivity, and flow meter, for instance, has been grouped together as it has all its parts as one single function that aligns well with the other functions. Similarly, the functions of receiving power, regulating power, and changing flow rate, heating, or cooling water, have been grouped together based on their similar purpose of powering and maintaining the system. Finally, the last grouping is focused on data recording and its correlation. Regarding the architecture, integration of most parts is necessary since the sensors, pump, and controller must be attached to the tubing where water comes in. The NMR also requires integration since it is the next stage after the sensors' data collection.

9.3 Interactions

The first interaction in our design pertains to the exchange of energy between the power source and the sensors, thereby affecting energy production and expenditure. At present, the power consumption of the sensors is unknown, and it is only after constructing the prototype that a power profile can be established by analyzing their interplay. The pump and sensors are the primary components that are influenced by the input power, and the addition of another pump after prototype development will depend on the power consumption of the existing components.

The computational aspect of our design is derived from the Atlas Scientific hydroponics kit. The sensors transmit data automatically to a server wirelessly via ThingSpeak. In the long-term perspective, the flow rate of the system will be instrumental in determining if the water has been effectively flushed from the NMR system for an accurate reading. Furthermore, the other sensed components will be discernible for comparison with NMR readings using ThingSpeak.

9.4 Geometric Layout

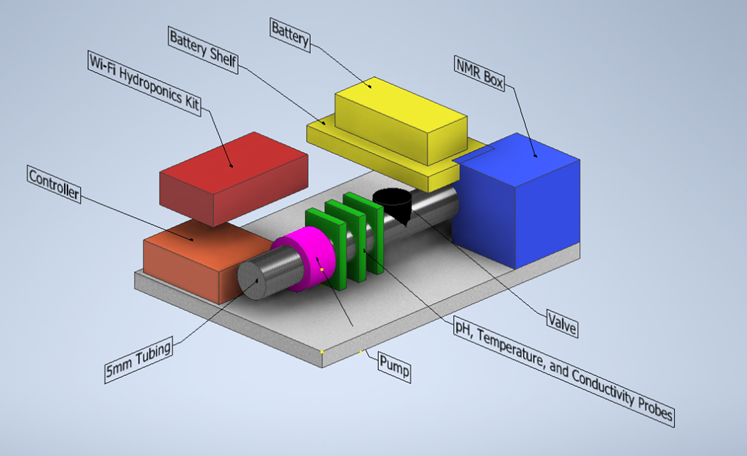
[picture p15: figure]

Figure 9.2: Geometric Layout for In Situ Water Quality System

The intended purpose of a geometric layout is to depict the integration and placement of various components within a design in a clear and labeled manner. Figure 2 displays the bin as a grey block located at the bottom. The walls of the bin have been removed to illustrate the location of other equipment within. An orange block represents the controller, which ensures continuous sampling of the water. The Wi-Fi Hydronics Kit, which includes three sensors, a temperature probe, a pH probe, and a conductivity probe, is depicted as a red block. The green blocks represent the sensors. The silver tube, approximately 5mm (about 0.2 in) in diameter, will allow water to flow through the bin and into the NMR box. A pump connected to the pipe is represented by the pink cylinder, while the black cylinder at the end of the pipe serves as a valve to regulate water flow. The yellow block displays the battery, which will be placed on a battery shelf. The battery will provide power to the water pump, the hydronics kit with the sensors, the controller, and the NMR box. Finally, the blue cube represents the NMR box.

10. Engineering Analysis

The purpose of performing engineering analysis is to serve as a warning of predictable failures or shortcomings in the design. Some potential problems are power supply and regulation, temperature regulation, head loss/pump inefficiency, and water damage to electronics. A failure mode and effects analysis (FMEA) considered the severity of each failure, the probability of occurrence of the failure, and how detectable each failure was, see Table 10.1. Some of the desired values sought after in the analysis were current to the pumps and the flow rate of the pumps while encumbered by the pneumatics of the rest of the design.

Table 10.1. Failure Mode and Effects Analysis

Failure Mode | Severity (1-10) | Occurrence (1-10) | Detection (1-10) | Risk Probability Number (1-1000)
Debris in the water blocking the tubing | 5 | 6 | 5 | 150
Head loss causing poor flow velocity | 4 | 4 | 6 | 96
Overheating of the box | 7 | 5 | 7 | 245
Casualty/loss of pressure in PVC or tubing | 4 | 4 | 7 | 112
Power outage | 5 | 4 | 1 | 20
Under or overpowering | 5 | 4 | 5 | 100
Water departure damaging electronics | 6 | 5 | 5 | 150
Sensor failure / poor calibration | 5 | 4 | 8 | 160

Power and Circuitry:

The design requires that several components are powered by the same 12V, 5A, 60W power supply. The current required to adequately power the microcontrollers will inevitably take away current passing through the pumps. Using Kirchoff’s Laws and Ohm’s Law, a circuit analysis will provide a basis for future improvement of the design. Table 10.2 outlines the variables in the equations governing this analysis.

Kirchoff Current Law Equation

[1] Iin = Iout

Ohm’s Law | Power Equation

[2] V = I*R | [3] P = I*V

Table 10.2. Variable Descriptions for Circuit Calculations

Variable symbol | Variable name/description | Variable units
Iin | Incoming current | Ampere (A)
Iout | Outgoing current | Ampere (A)
V | Voltage | Volt (V)
I | Electric current | Ampere (A)
R | Resistance | Ohm (Ω)
P | Electric power | Watt (W)

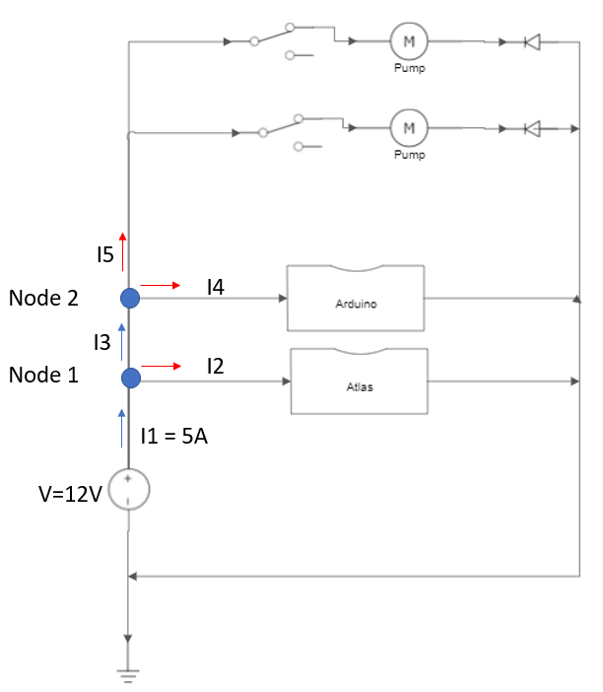
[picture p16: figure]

Figure 10.1. Circuit Diagram for Kirchoff’s Current Law

Calculations:

[4] Node 1: i1=i2+i3

[5] Node 2: i3=i4+i5

Arduino draws 0.200A at maximum power, and the Atlas Scientific controller draws 0.310A when operating. See Figure 10.1 for current pathways and the Current Law. Both values were obtained from their specifications on their respective company websites.

[6] 5A=0.200A+i3

[7] i3=4.800A

[8] 4.800A=0.310A+i5

[9] i5=4.490A

Using Kirchoff’s current rule, the allowable current that runs to the pumps, i5, is 4.490A. This current was to be split between the two pumps, controlled by normally open relay contacts that close when power is supplied by the Arduino (not pictured). Using the theoretical i5 and the circuit diagram with pumps in parallel, the maximum theoretical energy consumption and pump power to use in other calculations.

[10] P=(i5)/2*Vpump

[11] P=2.245A*12V=26.94W

The power drawn from each of these pumps is theoretically 26.94 Watts when running without variable control of the current.

Temperature Regulation

The design is exposed to the elements, in sunlight and overcast conditions. The box containing the electrical components is made of plastic, and an analysis of the temperature over time provided an idea of operating air temperatures within the box. Temperatures from each hour of the day for the past week were averaged together to produce a temperature vs. time graph. The weather conditions for the test were a combination of cold and rainy days in Table 10.3.

Table 10.3. Calculated weekly average temperature.

Time | | Avg. Temperature (Fahrenheit) | Mon, Jan 30 | Tue, Jan 31 | Wed, Feb 1 | Thu, Feb 2 | Fri, Feb 3 | Sat, Feb 4 | Sun, Feb 5
0:00 | 48.71428571 | | 49 | 62 | 62 | 50 | 41 | 37 | 40
1:00 | | 48 | 50 | 55 | 62 | 49 | 47 | 39 | 34
2:00 | | 48 | 49 | 56 | 62 | 48 | 47 | 37 | 37
3:00 | | 47.14285714 | 49 | 56 | 62 | 47 | 47 | 36 | 33
4:00 | | 47.14285714 | 49 | 56 | 62 | 47 | 47 | 35 | 34
5:00 | | 47.14285714 | 50 | 56 | 62 | 47 | 48 | 33 | 34
6:00 | | 46.71428571 | 49 | 56 | 62 | 46 | 48 | 32 | 34
7:00 | | 46.85714286 | 49 | 55 | 62 | 46 | 48 | 31 | 37
8:00 | | 46.85714286 | 49 | 55 | 61 | 46 | 48 | 31 | 38
9:00 | | 47.28571429 | 50 | 55 | 63 | 45 | 46 | 33 | 39
10:00 | | 49.14285714 | 52 | 56 | 66 | 45 | 47 | 36 | 42
11:00 | | 51.57142857 | 54 | 61 | 70 | 46 | 49 | 38 | 43
12:00 | | 54.14285714 | 57 | 61 | 73 | 46 | 52 | 41 | 49
13:00 | | 55.71428571 | 58 | 62 | 73 | 46 | 54 | 43 | 54
14:00 | | 57 | 60 | 65 | 72 | 46 | 56 | 44 | 56
15:00 | | 58 | 61 | 67 | 72 | 46 | 56 | 46 | 58
16:00 | | 57.57142857 | 61 | 67 | 67 | 46 | 55 | 48 | 59
17:00 | | 56.57142857 | 61 | 67 | 62 | 47 | 54 | 46 | 59
18:00 | | 54.14285714 | 59 | 65 | 58 | 47 | 51 | 44 | 55
19:00 | | 51.71428571 | 54 | 63 | 55 | 47 | 49 | 42 | 52
20:00 | | 50.85714286 | 56 | 62 | 53 | 47 | 47 | 41 | 50
21:00 | | 49.28571429 | 55 | 61 | 52 | 47 | 45 | 40 | 45
22:00 | | 48 | 55 | 61 | 51 | 47 | 43 | 36 | 43
23:00 | | 47.85714286 | 56 | 62 | 50 | 47 | 42 | 37 | 41

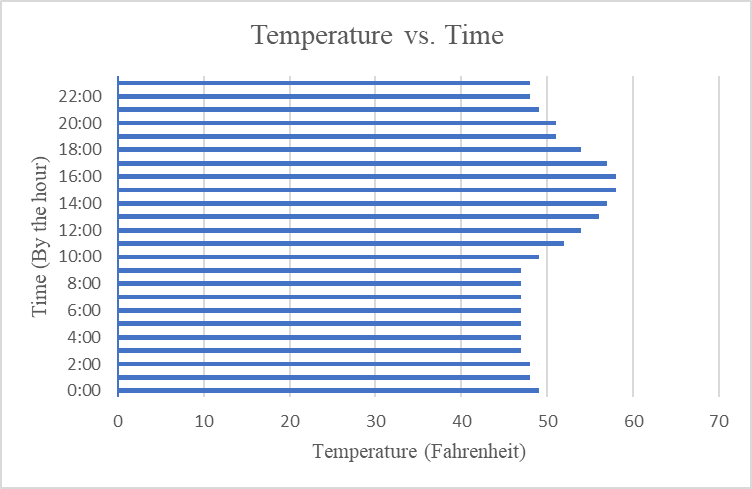
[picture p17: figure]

Figure 10.2. Graph of Temperature relative to time.

The maximum air temperature recorded was 58 degrees Fahrenheit in Figure 10.2. The temperature of the box and its components were expected to be higher than what was recorded, because the analysis was performed neglecting the heat added by the components, as well as the radiation heat transfer from the sun. The overcast conditions in the testing week is also likely to have decreased the average temperature recorded. The conditions were not expected to exceed the microcontroller’s operating temperatures at a much higher 85 degrees Celsius.

*Note: this analysis was performed before the implementation of a voltage regulator, which added a significant amount of local heat to the circuit board in contact with the pump’s microcontroller.

Pressure Calculations

The length of tubing and force of gravity will undoubtedly cause pressure changes on the pumps and within the sensing tube. Theoretically, there will be loss from both the pumps and the altitude gained by the water. Using Bernoulli’s Principle, these losses can be calculated. However, some liberties have to be taken in the analysis, assuming that the water is pure, coming from a reservoir with no flow, and the system is in steady state. The closest our design will get to these theoretical values is after the pumps have been running for a few seconds. See Figure 10.3 and Table 10.4 for reference in the Bernoulli Equation calculations.

Figure 10.3. Reference Image for Bernoulli Principle

Table 10.4. Variable descriptions.

Variable symbol | Variable name/description | Variable units
P | Pressure | Pa
ρ | Density of fluid | kg/m^3
ν | Fluid velocity | m/s
g | Acceleration due to gravity | 9.81 m/s^2
h | Height | Meters (m)

Bernoulli’s Equation

Assuming steady state flow, the pressure difference between point one and two is:

[12] ∆P=1/2ρv_1^2 +ρgh_1 -1/2ρv_2^2 - ρgh_2 +(head loss)

Density of water at 20C is 0.998 kg/m^3, and the pumps produce 500mL/min flow rates. For calculating pressure loss due to height, assume that the velocities are the same at position 1 and two. The ground where the box is placed is elevated about a meter above the water. The outlet of the box is 20cm from the ground. That makes h1 = 0 and h2 = 1.20m.

[13] ∆P=ρgh_1 - ρgh_2

∆P=- 11.2 N/m^2

Theoretical pressure drop between the reservoir and the second position is 11.2 Pascals. The head loss from the pumps can be determined in future testing, by gauging flow rate out of the design. For this analysis, frictional losses cannot be calculated with any precision, so they aren’t included. However, it is a theoretical pressure drop and the actual value is likely more based on the turbulence of flow of the water.

Power Restrictions

After the circuit analysis, a better understanding of the power restrictions can be cultivated. Using the current in each of the components from the circuit analysis, Ohm’s Law, and the Power Equation, the energy required to support each component can be derived in Watt Hours (Power*Time). Currently, the power source is plugged into the wall and runs at 60W 12V 5A. This is an important analysis to perform because if one component drastically affects the energy consumption of the prototype, a revision in equipment may improve the design.

Ohm’s Law | Power Equation

[2] V = I*R | [3] P = I*V | [14] E = Power*Time

Table 10.5. Variable descriptions.

Variable symbol | Variable name/description | Variable units
V | Voltage | Volts
I | Current | Amperes
R | Resistance | Ohms
P | Power | Watts
E | Energy | Watt Hours

Calculations:

[14] Pump: E=P*t

Recall theoretical power of a pump is 26.94W. The pumps will only be running one out of every 6 minutes, 0.1266 hours of time running per hour. The microcontrollers will be running constantly to keep time and transmit data on the fluid below. If the power supply (not a battery) functions well with this design, then a battery with the similar output parameters and a 1260Wh capacity could allow us the following amount of functioning time:

[15] t=E/P

t=1260/60hours = 21 hours

The value in finding energy expenditure is that most batteries are rated in W*h. The amount of electricity still in a battery will diminish over time, and given the pumps are the highest power consuming component, the energy expenditure is important to know. The Watt*hours of some commercial car batteries is about 1260.

The calculated time, 21 hours, is the length of time that the design can run with all systems running, including the pumps. The wattage of the design when the pumps aren’t running is:

[16] P=2P(pump)+P(controllers)

60W = 2(26.94W) + P(controllers)

Pcont. = 6.12W

Therefore, the total time that the design runs, assuming no losses, is:

[17] t=1260/(60*.1266+6.12*.744)hours

t=103.709 hours

This gives the design a little more than three days of operational time using a commercial car battery. However, during prototyping, the design will be powered by a conventional power supply, not a battery.

*Note: The final presentation of the design ran on a much smaller wattage and a longer measurement interval, vastly increasing the operational time of the design, because of this analysis.

11. Manufacturability

The aspects that regard optimizing production of the product are:

Component selection (Power Supply)

The original power supply was a 60-Watt, but it must be custom made. Instead, a 50-Watt power supply is more abundant. This will change slightly change the design because the 50-W is smaller than the 60-W.

Table 11.1: Comparison of 50-W and 60-W power supplies

| 50-W | 60-W
Item #: | LRS-50-12 | RS-100-12
Price: | $12.90 | $24.40
Size (LxWxH): | 2.00’’x1.00’’x0.40’’ | 6.26’’x3.80’’x1.5’’
Output Current: | 4.200 Amps | 8.500 Amps
Max Power: | 50 Watts | 102 Watts

By switching from a 60-Watt power supply to a 50-Watt power supply, money is saved. Also, there are more options for the placement of the power supply since it is smaller than the original. The 50-Watt loses some current output compared to the 60-Watt, but there is still enough current for the pumps and hydronics sensors.

Protection (Power Supply)

To protect all electrical components from water damage, a protective cover was designed. The inside would have a raised bottom for the power supply as well as a higher shelf designed for the voltage regulator. Holes would be drilled into a lip to secure to the platform. Other outlets would be made in order to have better wire security.

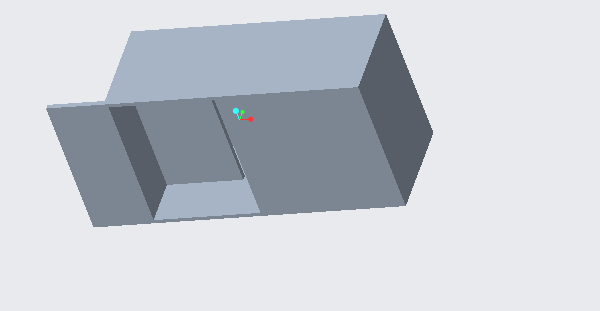
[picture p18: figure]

Figure 11.1: Power Supply Cover

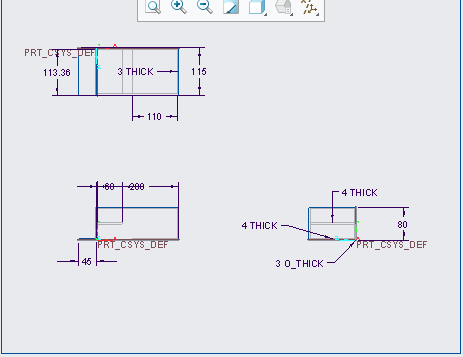
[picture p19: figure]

Figure 11.2: Power Supply Drawing

Stability (Hydronics Sensors)

The original concept for the sensor's stability was to drill a hole into the PVC waterflow pipe just wide enough for each sensor to fit snug.

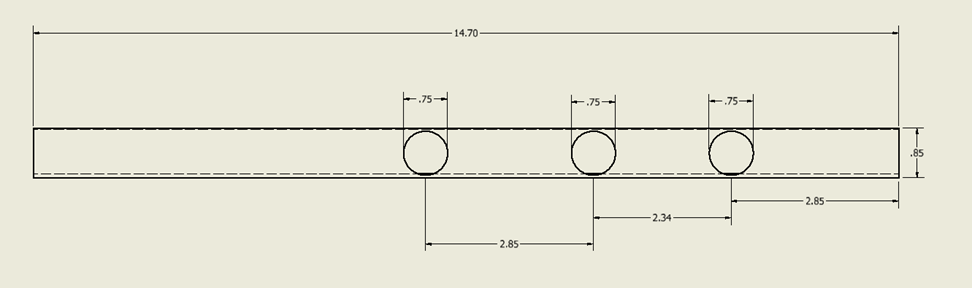
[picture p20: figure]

Figure 11.3: Previous PVC design (Dimensions in inches)

The new concept will use Cable Glands. The Cable Glands will be able to secure the sensors in place while they are collecting data. The Glands will be attached to a PVC Tee fitting.

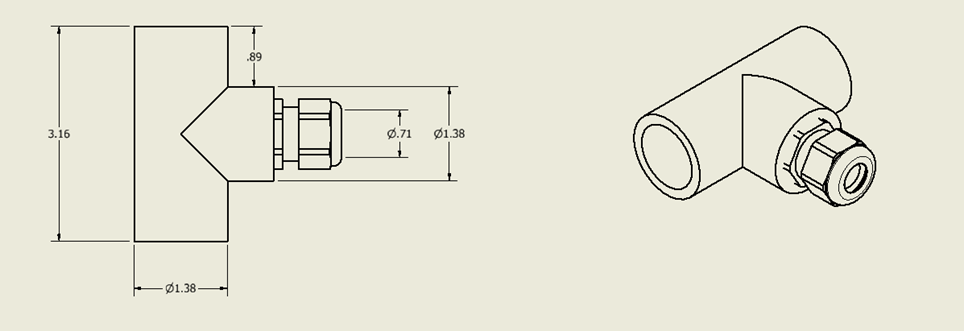
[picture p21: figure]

Figure 11.4: PVC Tee and Cable Gland assembly.

The result of this change will provide a tight and secure connection for the Hydronics sensors. This will provide a more accurate reading of the data as well as lowering the chances of failure.

Symmetry (PVC)

The previous PVC pipe used for waterflow had three holes, but they were drilled without precision relative to length. PVC Tees will separate the PVC pipe, but symmetry will be taken into effect with the length of each section of pipe. Figure 1 in the section above shows the original design for the PVC pipe.

The new concept will break the PVC pipe into 4 even parts with lengths of 2.63 inches. They will then be attached to three PVC Tees. The top of each Tee will have a Cable Gland screwed on.

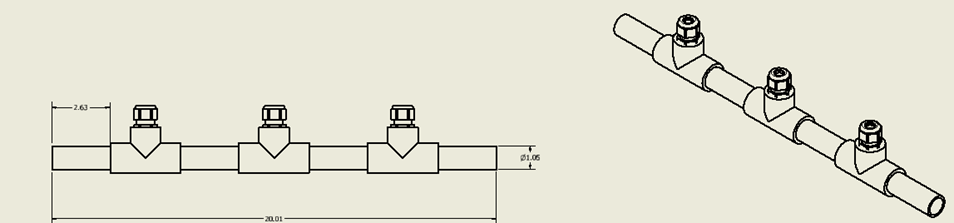
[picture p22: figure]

Figure 11.4: New PVC pipe design

This new concept has each Tee spaced evenly apart on the PVC pipe. This gives the design a uniform look and affects the sensors by spacing them out more letting them get more accurate readings.

Stability (Hook)

Hooks were designed to go to the end of each side of the platform. These simply designed hooks were created in order to hold the amount of tubing needed for pumping the water. This Would have a cleaner space for working and being able to interact with the actual probes and PVC.

Figure 11.5: Hook Design

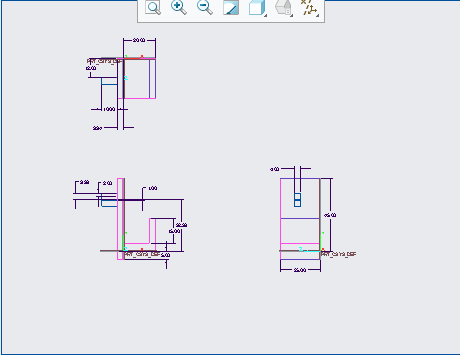
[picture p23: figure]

Figure 11.5: Hook Drawing

12. Product Cost/ Economic Analysis

An economic assessment is important because it can provide a way to predict costs and balance them against alternative courses of action. Money has a time value, is the leading concept in engineering economic analysis. All of the metrics of value that were analyzed are: coat of labor, cost of materials/components, and profitability of the product. A cash flow diagram can be used to deal with financial transactions taking place at various times in the future. A cash flow diagram is used in the report to show the cash inflows (such as sales) and cash outflows (such as capital investment) over an extended period of time. The key outcomes of this report include but are not limited to: Total cost of pneumatics/electronics/hardware for a single unit is $552.91, total cost per unit including labor is $652.91, and selling 3 or 4 units at $750 will recover the investment cost.

The idea of how the product will be used is to have clients use it for data collecting. The goal would be for not only the ARTS-lab, but other labs to be able to use our product to conduct experiments and gain results which we would then create a profit from. We will be assuming for this analysis a lifespan of 2 years, or 24 months (about 2 years). The main upfront cost for this project will come from the materials needed in order to manufacture the product. According to the standard cost per unit table, we have a total of $552.91 for production. This is distributed to Electronics, Pneumatics, and Hardware. The recurring cost includes maintenance, which includes the replacement of any part in the product like the sensors, probes, as well as the pumps and hardware. Taking into account prices for replacement, this can come out to if multiple replacements are needed to a possible $334.31 for the sensors and probes alongside an added number for hardware. This leads to training for future workers at an added $100. This is based on training time and work time in manufacturing the product

Analysis

Table 12.1 – Standard Cost per Unit

Electronics | Cost per unit $USD
50W Power Supply | 19.55
(2x) 12V DC Pumps | 73.98
Arduino Microcontroller | 29.95
Atlas Scientific Microcontroller | 379.99
(2x) Relay | 7.39
Subtotal Electronics | 510.86
Pneumatics | ------------------------------
PVC Base | 1.67
PVC Tees | 2.34
PVC to 5mm adapters | 1.67
PVC Probe Mounts | 10.64
5ft Silicone Tubing (may vary) | 11.79
PVC Risers | 1.56
Subtotal Pneumatics | 29.67
Hardware | ------------------------------
General Wiring | 0.31
Breadboard | 1.67
(6x) Nuts | 1.74
(6x) Washer | 3.16
(6x) Bolts | 0.58
Plastic Bin and Cover | 4.92
Subtotal Hardware | 12.38
Total | 552.91

The cost of components of our current prototype is shown in the Cost per Unit above. The total cost per unit omitting labor and incidentals is $552.91. The ARTS Lab prioritizes its purchases through Grangier, an industrial supply company whose website supplied the cost of materials. The only materials that were quoted at different prices were the power supply, Arduino, general wiring and the breadboard. All other pneumatic and industrial components were sourced through Grangier.

In addition to the cost of materials, time to produce and labor cost analyses were performed for the design. Under the assumption that the ARTS Lab covers expenses related to workspace and tool access, it would take an estimated 8 hours of physical work to produce each unit. If we were to hire a worker to perform that task, at $10/hour, with 2 hours of training in calibration and coding, the total cost per unit would be raised to $652.91 per unit.

Recovery of investment could be achieved after the sale of just three or four units at $750. The ARTS Lab already has the tools and facilities required to produce these products, and for us to do the labor ourselves, we would be making about $200 profit per unit sold. That would have us breaking even at about 3 months. For the sake of our theoretical analyses, we assumed that the ARTS lab would allow us to use their facilities for the next 12 months. Then, paying for a new space would affect the cash flow for our product in the next two years.

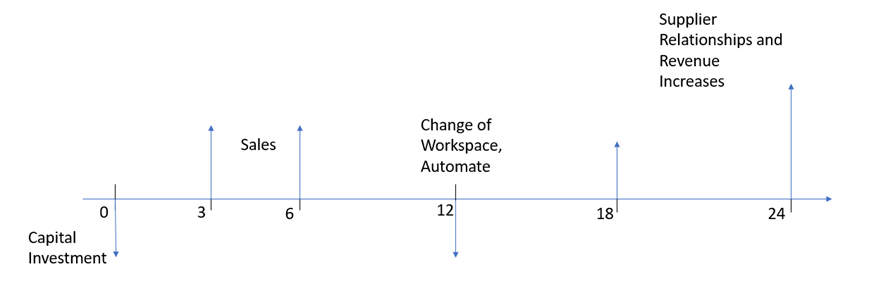
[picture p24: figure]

Figure 12.1- Cash Flow Diagram

The diagram above shows the cash flow of our product over the course of the next 24 months (about 2 years). It is important to note that these figures are subject to change based on variables that we can’t control, i.e., demand or supply chain problems. The flow is broken into 5 phases that have different costs associated with manufacturing and selling the product.

Phase 1 – 0-3 Months

Initial investment by Professor Downey and the ARTS Lab was the cost of the prototype: $552.91. In the first three months after the final product is created, the target number of sales is 40 units – slightly less than our production capacity to allow for incidental changes in the initial phases of the business. At month 3, if all units are sold, the business will have accumulated about $7,883.60.

Phase 2 – 3-6 Months

Months 3-6 are hopefully months where the cost of materials can be decreased via a relationship with vendors at Grangier or Atlas Scientific, or by buying more materials in bulk. Buying in bulk poses a problem with storage space in the lab, so that problem should be attacked soon. However, the product would continue to make gains without discounts.

Total at 6mo =~ $7,800 + (12 weeks) * ($197.09/unit) * (4units/week) =~ $17,260

Phase 3 – 6-12 Months

A decent profit has been achieved at this point and we would begin to look for space separate from the ARTS Lab so that they can continue with their work without manufacturing operations taking place. A reinvestment in the product and business would make the business more sustainable. To rent an 800 square foot office space in Columbia, we found that the cheapest option amounts to about $750/month. We assume that moving operations in this phase will cut down production and we will lose some money buying the tools and equipment to manufacture in this space. We estimated that a soldering iron, tables, drills and tools would cost about 200$. If we made the move at 12 months, the following calculations could be applied.

Total at 12 months = ~$17,260 + $18,920 (6-12 profits) – $750*12months (rent) – $250 (tools)

= ~$26,930 remaining after moving, paying a year lease, and buying equipment.

Phase 4 and 5 – Beyond

As the business grows, we have the funds to improve the design and could potentially upcharge the product as well as hire workers to produce it. We would pay laborers $10/hour and would attempt to improve profit per unit to roughly $225/unit via business relationships with suppliers or by improving the design to optimize for cost.

After 2 Years Total: ~$26,930 + (12 months operation) (16 units/month) ($225 profit/unit)

= ~$43,200

The net present worth of the business (if we were to sell this commercially) is represented by the net inflow subtracted by net outflow. The current amount spent on this product is the cost of materials: $552.91. After refinement of the prototype, this cost is subject to change, but we would start the price for our product at $750 per unit. Charging sales tax to the customer, our profit would be $197.09 per unit. If we could produce 4 of these per week, $3153.44 is the profit after a month of selling if demand meets supply.

Conclusions/Recommendations

An economic analysis is crucial because it may help forecast expenses and weigh them against potential alternatives to a course of action. The suggested fixture, in sum, is a useful addition to the ARTS Lab. Not only is it anticipated to boost annual profits, but it also lowers risk, both indicate profitability in this project. The internal rate of return and net present value for this project were calculated using criteria such as price per unit, upfront costs, and time to break even. The investment might be recovered once just three or four units at $750 are sold. The ARTS Lab already has the equipment and resources needed to create these products. A final suggestion would be that while we have to idea to move to an office space to help in manufacturing, considering the cost of moving any equipment from the lab would probably be needed.

Appendix/References

[1] Office Space Rental Reference - https://www.loopnet.com/Listing/2754-2772-Rosewood-Dr-Columbia-SC/22382902/

[2] Probe and Sensor References - https://atlas-scientific.com/ph/

- https://atlas-scientific.com/temperature/

- https://atlas-scientific.com/kits/conductivity-k-1-0-kit/

13. Testing

To engineer and quantitatively define the shortcomings of the design, different methods of testing were done. Testing parameters were chosen based on criticality to design function. The volumetric flow rate, average power consumption, water leakage, and running time without maintenance were tested rigorously. The parameters mentioned are a part of the target specifications in Table 13.1

Table 13.1. Table of target and fallback specifications.

Metrics | Units | Target Specification | Fallback
Measures conductivity | micro Siemens/cm | 15 | 5-60
Measures pH | none | 7 | 6.5-7.5
Measures temperature | [C] | 22 | 19-25
Measures flow rate | [lpm] | 0.57 | 0.50-0.64
Electrical components must stay dry | [Boolean] | True Positive | TP - TN
Temperature regulation near operating temperature of electrical components | [C] | 23 | 40 - 60
Fluid temperature change over time | [C/min] | 5 | 20
Data sets per unit time | [data sets/min] | 0.2 | 0.1
Time without maintenance | [days] | 10 | 2 - 6
Portability | [lb.] | 40 | 25 - 55
Average Power consumption | Watts | 6.5 | 5.0 - 8.0

Volumetric flow average

The target value is 0.57 L/min while the fallback value ranges from 0.50-0.64 L/min.

Equipment: Pumps, Metered Beaker, Bucket of Water

Procedure: Set the microcontroller to run the pumps in 10 second intervals. Put the inlet tubing into the water bucket. Completely purge the system of any air before taking readings. To take a reading, insert the outlet tubing into the empty metered beaker. Allow the pump to run for its allotted cycle time and record the volume of water in the graduated cylinder.

Table 13.2: Volumetric Flow Rates

Time (min) | Volume (mL) | Flow Rate (L/min)
0.17 | 85 | 0.51
0.17 | 92 | 0.552
0.17 | 90 | 0.54
0.17 | 91 | 0.546
0.17 | 94 | 0.564
0.17 | 95 | 0.57
0.17 | 96 | 0.576
0.17 | 96 | 0.576
0.17 | 97 | 0.582
0.17 | 96 | 0.576
0.17 | 95 | 0.57
| AVG (L/min) | 0.560

Equations Used: Flow Rate Q=Volume/time

Average power consumption

The target value is 6.5 Watts while the fallback value ranges from 5.0-8.0 Watts.

Equipment: Variable Power Supply

Procedure: Attach the 12V DC leads from the voltage regulator to the power supply [out]. Adjust the variable power supply to a 12V 60W signal and turn on the output. While the prototype runs, take intermittent values of output wattage from the power supply screen. Take note whether the pumps are running or not for each power reading.

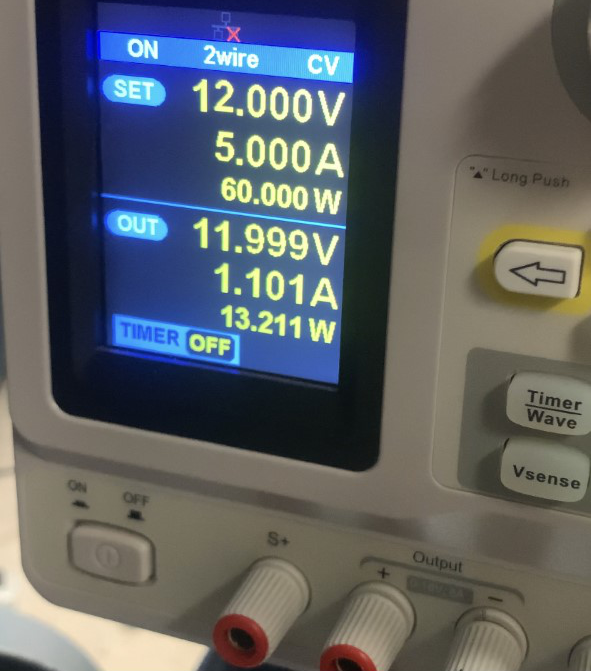
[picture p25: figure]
Image preview

Figure 13.1. Variable Power Supply

The wattage of the prototype was vastly lower than the initial ceiling of 50W provided by Professor Downey. In Figure 13.1 the output wattage was 13.211W, the maximum wattage obtained while the pumps were running.

Water leakage

The target value is True positive while the fallback value is true positive-true negative.

Equipment: Paper Towel, Metered Beaker

During the first testing attempts, the sources of water leakage were identified and fixed. The barbs connecting the tube to PVC were exchanged with cable glands to prevent a casualty. Once the initial flooding was fixed, the area around the sensing components was dried to ensure that there were no other leaks in the system.

In the later, outdoor endurance testing, the design was exposed to proper operating temperatures and pulled samples from a canal. At the maximum temperatures of the day, the design displayed absolutely no leaking. If a leak had been detected, the water in the box is to be poured into the metered beaker. That volume divided by the time the prototype operates is the specification value for water leakage. For the outdoor endurance test, that was 0 L/min.

Running time without maintenance

The target value is 10 days (about 1 and a half weeks) while the fallback value ranges from 2- 6 days. The system is developed and designed to work without maintenance for a period of 10 days. Unfortunately, due to security concerns and operator time constraints, it was only tested for 4 hours, and not for a full 10-day duration. During the testing period, the system performed decently within reason for the time it ran.

Although it was not a previously targeted specification for testing, more conclusions were made based on sampling data during the endurance testing. See Figure 13.2 for the conductivity data. The first noticeable issue was the variance in the conductivity probe’s sensing. There is a problem with the orientation of the probe that produces an air bubble in the sensing component. This is a foreseeable issue in the Atlas Scientific datasheet, Appendix A. The stabilization of the conductivity readings is not a result of the sample, but the air bubble produced by the pumping of water into the PVC pipe.

Figure 13.2: Graph of Conductivity

Furthermore, the conductivity probe did not have ample time to stabilize readings between sampling intervals – the amount of time for sensing before a new sample is pumped into the PVC pipe. The temperature at peak hours of the day is speculated to have disabled the Arduino from controlling the pumps when left idling for more than 3 minutes.

The data from the pH and temperature sensors are also clearly affected by the limited sampling time and high temperatures of midday, as show in Figures 13.3 and 13.4. The temperature readings appear to increase within the sampling time, indicating poor insulation in the sensing tube. A close look at the pH readings shows that stabilization occurs just before the next sampling cycle.

Figure 13.3. Temperature Readings

Figure 13.4. pH Readings

14. Final Design

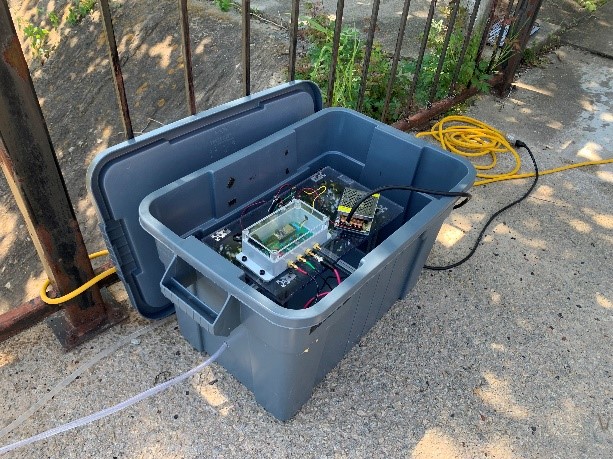
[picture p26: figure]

Figure 14.1. Design Photo

In Figure 14.1, a photo of the final design sampling water is provided. The design features a 12V power supply capable of supporting 60W, which powers two microcontrollers that control the pump running intervals, data collection, and transmission. Figure 14.3 is a diagram for the PERF board and voltage regulator that allows the microcontrollers to function on the same power supply as the 12V peristaltic pumps. An Arduino Nano is responsible for controlling the pumps and keeping time for sampling intervals. The Atlas Scientific Hydroponics Kit in Figure 14.2 is responsible for the sampling, calibration, and transmission of data to a server via ThingSpeak, a data aggregation software through MathWorks.


Figure 14.2. Atlas Scientific Hydroponics Kit (See Appendix A)

Figure 14.3. Circuit Diagram


Figure 14.4. PVC Tees with Cable Glands for probes

The probes that collect data on the water samples are mounted on a PVC assembly (Figure 14.4) secured to an aluminum frame. The cable glands are screwed tightly to prevent leaks and ensure the probe is completely wetted. This design makes calibration of the probes simple, and each of the probes easily replaceable. The components for the sensing pipe and the rest of the prototype are in Figure 14.1

Table 14.1. Bill of Materials

Electronics | Pneumatics | Hardware/Tools
60W Power Supply | PVC Base ½ in | Gauge 20 Wiring
(2x) 12V DC Pumps | PVC Tee x3 | Soldering Iron
Arduino Microcontroller | PVC Cable Glands x5 | Nuts x12
Atlas Scientific Microcontroller | PVC Primer and Glue | Washer x12
Temperature Probe | 5mm Tubing (as needed) | Bolts x12
Conductivity Probe | | Plastic Bin and Cover
pH Probe | | Extruded Aluminum
PERF Board
12V-5V Voltage Regulator

15. Conclusions on Designed Products

This design is excellent at providing fresh samples, without leaks, and within given power requirements. Although it does those things well, there are pitfalls in the design that prevent the appropriate sampling procedures from taking place. For example, temperature in the box when exposed to sunlight at the top of the day prohibits the design from pumping fresh samples after idling for more than three minutes. The three minute pause is just barely substantial for getting stabilized measurements from the Atlas Scientific probes.

Another casualty of the heat is the temperature of the water being sampled. Water in the silicone tube as well as within the PVC pipe in idle will retain heat. There is very little insulation where the measurements are taking place, so an increase in the temperature is apparent from the sensor’s data in the testing chapter (Ch.10).

In future iterations of the design, two main problems must be addressed. The first is the inability of the pumps to run if left to rest in a charged state for longer than 3 minutes. The pumps must keep water static in the assembly long enough to generate a stable reading. To troubleshoot the pneumatic problem, it is recommended to test the design by changing the height at which sample water exits the box. Also, test for current supply when the voltage regulator is operating at high air and local temperature.

The second issue to address is the air pocket that essentially disables the conductivity probe. There could be a simple solution as easy as reorienting the PVC or probes to get a better reading. The other solution would be to change the design entirely to an internal reservoir concept referenced in concept selection matrix, where probes would take readings from a static reservoir that drains after sufficient sampling has taken place.

Table 15.1. Satisfactory Needs

The specifications that we retained from the sponsor are listed in Table 15.1. In the future of this project, more metrics are going to be required to have a successful product. To find and retain accurate specifications and fallback values, a control must be used, particularly with the sensors for pH and conductivity. For example, there was no way to confirm the actual pH, conductivity, or temperature of the water being sensed. More rigorous testing of the probes, in different arrangements, will likely result in a more effective design. To do this, it is recommended a control sensor suite is used.

The primary lesson this team learned is that free networking is the key to rapid progress in design. Putting as many eyes as possible on a concept is an excellent way to gain new perspective. It was also discovered that changes in a design can be rapid and drastic, but it will influence quantitative analysis if the changes aren’t documented properly. In the future, proper documentation practices in coordination with good teamwork will be the key to our success.

16. Acknowledgments

We would like to thank Professor Downey and Professor Sabalowsky for their guidance on this Senior Design project. We would also like to profusely thank the ARTS Lab for their hospitality in their space. Particularly we would like to thank Ryan, Mohammed, and Joe from the lab for their help in obtaining tools and materials to fabricate the design.

17. Appendix

[A] Atlas Scientific Hydroponics Kit Datasheet – https://files.atlas-scientific.com/Wi-Fi-Hydroponics-kit-setup-guide.pdf

[B] The Complete Phase Diagram of Monolayers of Enantiomeric N-Stearoyl ... https://pubs.acs.org/doi/10.1021/acs.langmuir.2c01936.

[C] “Conductivity Measurement & Testing: Thermo Fisher Scientific - US.” Conductivity Measurement & Testing | Thermo Fisher Scientific - US, https://www.thermofisher.com/us/en/home/life-science/lab-equipment/ph-electrochemistry/conductivity-measurement-testing.html.

[D] Dabadi), Sadrish. “Ph Values of Water with Ph Level Chart.” Earth and Human, 11 June 2022, https://earthandhuman.org/ph-values-of-water/#:~:text=Different%20pH%20Levels%20of%20Typical%20Materials%20%20,%20Approx.%207.5%20%203%20more%20rows%20.

[E] Friedman, Daniel J. “Building Water Flow Rate Calculation & Measurement Procedures Thanks to Shelly Weinberg.” Water Flow Rate Calculation & Measurement Procedures Shelly Weinberg and Daniel Friedman, Daniel J. Friedman at InspectApedia.com, https://inspectapedia.com/water/Water_Flow_Rate_Measurement.php#:~:text=Nominal%20%26%20Peak%20Water%20Pipe%20Flow%20Rates%20,%20%203000%20%209%20more%20rows%20.

[F] Klements, Michael. “How Long Can an Arduino Run on Batteries? I Tested 6 of the Most Common Boards.” The DIY Life, 17 Aug. 2020, https://www.the-diy-life.com/how-long-can-an-arduino-run-on-batteries-i-tested-6-of-the-most-common-boards/#:~:text=As%20expected%2C%20this%20board%20draws,Next%20we%20have%20a%20Nano.

[G] Mlblevins. “Density of Water at Room Temperature.” Science Struck, 20 Dec. 2010, https://sciencestruck.com/density-of-water-at-room-temperature.

[H] “Referencing of the Chemical Shift Scale in the NMR Data.” NMR Wiki RSS, http://nmrwiki.org/wiki/index.php?title=Chemical_shift_referencing.

[I] “What Is the Right Temperature Set Point for an Electrical Enclosure?” ACHR News RSS, ACHR News, 21 June 2019, https://www.achrnews.com/articles/141465-what-is-the-right-temperature-set-point-for-an-electrical-enclosure#:~:text=The%20acceptable%20operating%20temperature%20for%20most%20electrical%20devices,maintenance%20burden%2C%20and%20can%20actually%20pose%20operational%20threats.

[J] “Wi-Fi Hydroponics Kit.” Atlas Scientific, https://atlas-scientific.com/kits/wi-fi-hydroponics-kit/.

# [K] CA2968582C - Nuclear magnetic resonance apparatus, systems and methods

https://patents.google.com/patent/CA2968582C/enq=nuclear+magnetic+resonance&oq=nu clear+magnetic+resonance

[L] US9005416B2 – pH sensor

US9005416B2 - pH sensor - Google Patents (https://patents.google.com/patent/US9005416B2/en?q=ph+sensors&oq=ph+sensors)

[M] US8136414B2 – Flow metering

US8136414B2 - Flow metering - Google Patents (https://patents.google.com/patent/US8136414B2/en?q=dp+meter&oq=dp+meter)

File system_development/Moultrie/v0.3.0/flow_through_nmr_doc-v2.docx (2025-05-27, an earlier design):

Flow-Through NMR

LabVIEW Code:

The LabVIEW code features 1 main .VI file that utilizes 3 sub .VI files. The main VI file inputs the starting Larmor Frequency and the pulse file and immediately starts the Larmor Optimization sub-VI file. This sub VI takes measurements at, above, and below the starting Larmor Frequency and outputs the one with the best signal, each time calling a spin echo amplitude extraction VI file that takes the initial amplitude of the spin echo. The main VI then calls a T2 curve VI which is almost exactly the same as the VI we use for normal NMR that returns a T2 curve. The main VI allows you to change the number of data points averaged for each T2 curve for this VI as well as the number of T2 curves that are saved for each iteration of the main VI. Each iteration of the main VI consists of a Larmor Optimization phase followed by a T2 curve saving phase. So if you have a number of samples of 4 and a number of loops per iteration of 4, the code will be collecting 16 samples and saving 4 curves for each time it optimizes Larmor Frequency.

Running NMR:

To actually run the NMR, the first thing you need to do is set up the system. This will be the same as normal NMR, except the main difference is that rather than having a static sample tube, pumps are used with a tube to consistently change the sample. All of it is in the fridge except for the magnet. The coil and the coil holder CAD piece are in the NMR toolbox. The coil PCB needs an SMA connector to be soldered on and it will need to be calibrated like in the HardwareX paper. The pumps are hooked up to an Arduino that has them set to run for a set amount of time and then off for a set amount of time. We were working with controlling it via LabVIEW, but it was inconsistent and weird and the Arduino connection just wasn’t reliable so we stopped and just made it fixed time intervals.

To conduct NMR the first step is to plug in the power supply that connects both to the pumps and the PCB. This will turn the pumps on. Do not plug in that power supply unless you are ready for pumps to bring in water. At this time you can start the NMR code and begin collecting data. Be sure to check in on the process every now and then to be sure the spin echoes are still visible. If not, unplug the power supply, force the code to stop, find the Larmor frequency, and run the code with a new folder to save data in. The power supply we use for this is an NI power supply – I believe it is in the wind tunnel lab, it is a thick black cord you can plug into a power strip.

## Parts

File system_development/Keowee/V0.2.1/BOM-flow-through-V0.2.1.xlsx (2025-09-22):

Designator | Component | Amount | Individual Cost | Total Cost | Vendor 1 | Vendor 2 | Vendor 3 | Vendor 4 | Vendor 5 | Vendor 6
Cells | Samsung 30Q | 10 | $8.22 | $82.20 | https://www.batteryjunction.com/products/samsung-30q-18650-3000-flat |  | https://www.ebay.com/itm/254630577493?chn=ps&google_free_listing_action=view_item&gQT=2
power plut | Powerwerx PanelPlateSB1 for Anderson SB50 Series Connectors | 1 | $9.99 | $9.99 | https://powerwerx.com/anderson-sb50-panel-chassis-mount
Box | RITTAL Enclosure: Steel, 15 in x 13 in x 10 in, NEMA 4, Solid Cover, Hinged | 1 | $234.98 | $234.98 | https://www.grainger.com/product/RITTAL-Enclosure-Steel-5AAC4?opr=ILOF |  | https://www.ebay.com/itm/185777140664?itmmeta=01JXJF02RJ2SD81DKBZE32WGPJ
Controller | cRIO-9054 | 1 | $3427.00 | $3427.00 | https://www.ni.com/en-us/shop/model/crio-9054.html
strain DAQ | NI-9236 | 1 | $3048.00 | $3048.00 | https://www.ni.com/en-us/shop/model/ni-9236.html
 |  |  | Total | $6802.17

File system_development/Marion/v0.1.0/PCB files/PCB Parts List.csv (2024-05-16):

Material Ordering List
Part Name
Pump Power PCB | Manufacturer Part # | Digikey Part # | Supplier | Code on Schematic
Barrell Jack | PJ-102B | CP-102B-ND | CUI Devices | N/A
2 Hole Screw Terminal | 282836-2 | A98076-ND | TE Connectivity AMP Connectors | N/A
4 Hole Screw Terminal | 282836-4 | A98078-ND | TE Connectivity AMP Connectors | N/A
Datalogging PCB | Manufacturer Part # | Digikey Part # | Supplier | Code on Schematic
3.3 V Linear Regulator | TC2014-3.3VCTTR | TC2014-3.3VCTTR-ND | Microchip Technology | U1
Capacitor SMD | CL10B105KP8NNNC | 1276-1946-2-ND | Samsung Electro-Mechanics | C1 / C2
SD Module | B0B5H3421M | ASIN (Amazon) | AOICRIE | Micro_SD1
Real Time Clock Module | B08XQ8TT7Z | ASIN (Amazon) | AOICRIE | RT1
Ultrasonic Sensor | B0C73XZRFQ | ASIN (Amazon) | Shutao | US1
3 Screw Hole Terminal | 282836-3 | A98077-ND | TE Connectivity AMP Connectors | N/A

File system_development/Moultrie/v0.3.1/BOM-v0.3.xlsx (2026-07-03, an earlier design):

Designator | Component | Amount | Individual Cost | Total Cost | Vendor 1 | Vendor 2 | Vendor 3 | Vendor 4 | Vendor 5 | Vendor 6
DIN rail power supply | MEAN WELL USA Inc. 1866-3518-ND | 1 | $29.30 | $29.30 | https://www.digikey.com/en/products/detail/mean-well-usa-inc/NDR-120-24/7705220
DIN Rail | APPROVED VENDOR Mounting Track: DIN Rail Mounting, Aluminum, 35 mm Wd, 305 mm Lg | 1 | $4.09 | $4.09 | https://www.grainger.com/product/Mounting-Track-DIN-Rail-Mounting-18Z759
PLA | PLA Basic - red | 1 | $19.99 | $19.99 | https://us.store.bambulab.com/products/pla-basic-filament?id=40475107000456
Box - external parts cover | SSI SCHAEFER Straight Wall Tote: 8.8 gal, 19 in x 13 in x 12 in, Stacking Capable, Blue | 1 | $64.82 | $64.82 | https://www.grainger.com/product/SSI-SCHAEFER-Straight-Wall-Tote-8-8-gal-9LEZ8?opr=ILOF
Extruded aluminum | T-Slotted Framing, Single Four Slot Rail, Silver, 20 mm Square, Solid, 10 ft | 2 | $34.04 | $68.08 | https://www.mcmaster.com/products/aluminum-extrusions/t-slotted-framing-rails-1~/
Aluminum plate | Multipurpose 6061 Aluminum Sheet, 1/8" Thick, 12" x 12" | 2 | $31.94 | $63.88 | https://www.mcmaster.com/products/aluminum-plates/multipurpose-6061-aluminum-sheets-and-bars-7/
Threaded inserts | Stainless Steel Helical Insert, M5 x 0.8 Thread Size, 5 mm Long, Pack of 10 | 2 | $3.38 | $6.76 | https://www.mcmaster.com/products/threaded-inserts/threaded-inserts-3~/stainless-steel-helical-inserts-9/thread-size~m5/
80/20 brackets | 10 S / 25 S 2 Hole Inside Corner Gusset | 25 | $5.45 | $136.25 | https://www.alufabinc.com/product/10-s-25-s-2-hole-inside-corner-gusset/
80/20 fasteners | 18-8 Stainless Steel Low-Profile Socket Head Screws with Hex Drive, M5 x 0.8 mm Thread, 10 mm Long, Pack of 50 | 1 | $12.10 | $12.10 | https://www.mcmaster.com/products/screws/socket-head-screws-2~/thread-size~m5/18-8-stainless-steel-low-profile-socket-head-screws/
80/20 T-nut | Roll In T-Nut: 15 Series/40 Series, M5 Fastener Thread Size, For 8 mm Slot Wd, Single Offset, 4 PK | 13 | $6.78 | $88.14 | https://www.grainger.com/product/FATH-INC-Roll-In-T-Nut-15-Series-40-55MT17?msockid=072e03e7d7f269131431162fd60e6862
Socket head cap screws | Socket Head Cap Screw: M5-0.8 Thread Size, 30 mm Lg, Std, Black Oxide, Steel, Class 12.9, 100 PK | 1 | $17.04 | $17.04 | https://www.grainger.com/product/Socket-Head-Cap-Screw-M5-0-26LG30?msockid=072e03e7d7f269131431162fd60e6862
plastic shelf material | HDPE Sheet: 0.25 in Thick, 12 in x 24 in, Opaque, Black, 4,600 psi Tensile Strength, 1.94 ft-lb/in | 2 | $12.24 | $24.48 | https://www.grainger.com/product/HDPE-Sheet-0-25-in-Thick-1ZAW2
Relay Module | 12V 1 Channel Relay Module with Optocoupler Isolation High/Low Level Trigger | 5 | $1.22 | $6.10 | https://www.ebay.com/itm/166286100101?chn=ps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
 |  |  | Total | $541.03
 |  |  | Total | $1082.06

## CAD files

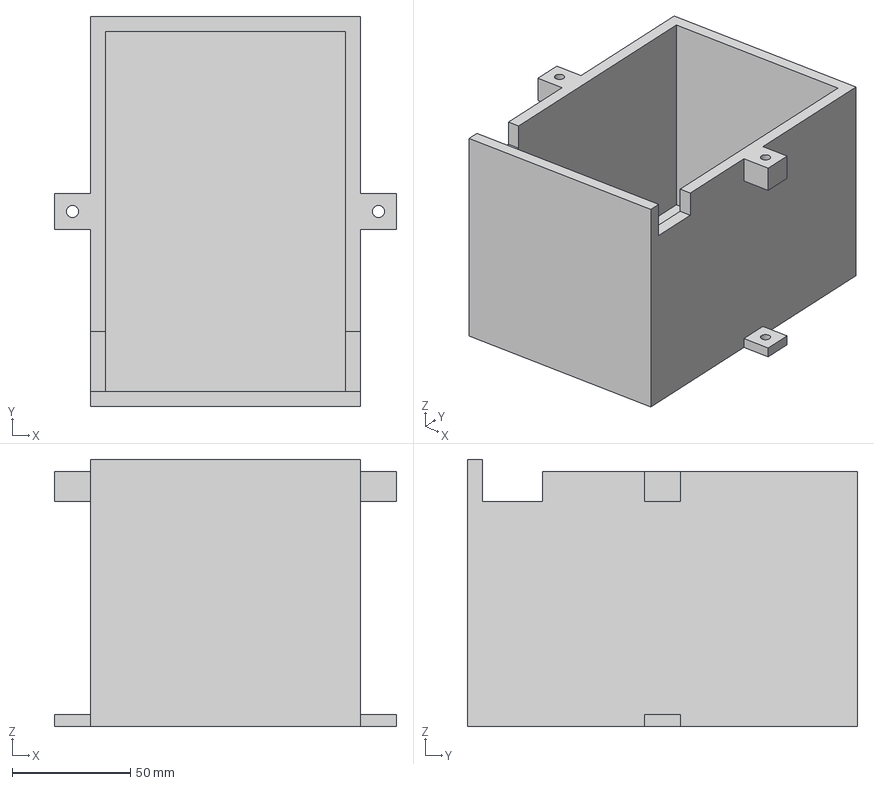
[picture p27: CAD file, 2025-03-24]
system_development/Keowee/V0.2.1/Solar_Panel/3D Prints/battery case holder.3mf
144.8 x 165.1 x 113.0 mm

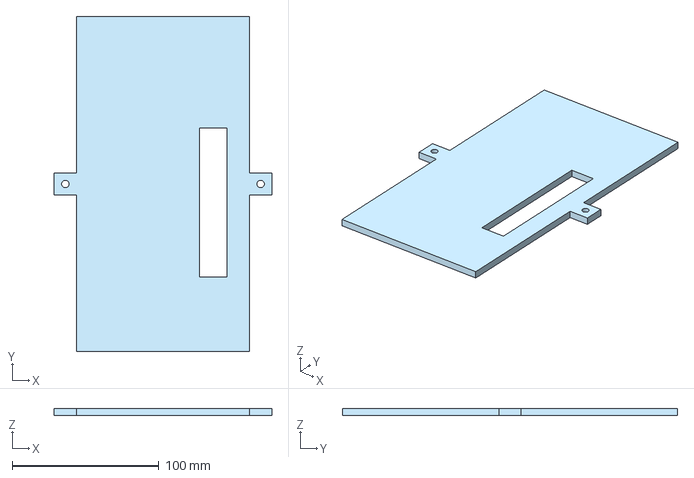
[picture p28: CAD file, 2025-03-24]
system_development/Keowee/V0.2.1/Solar_Panel/3D Prints/power output lid.3mf
148.6 x 228.6 x 5.08 mm

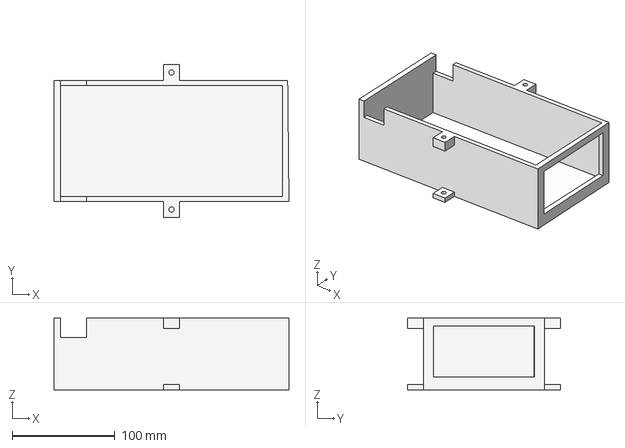
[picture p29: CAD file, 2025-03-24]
system_development/Keowee/V0.2.1/Solar_Panel/3D Prints/power output frame.3mf
228.6 x 148.6 x 69.8 mm

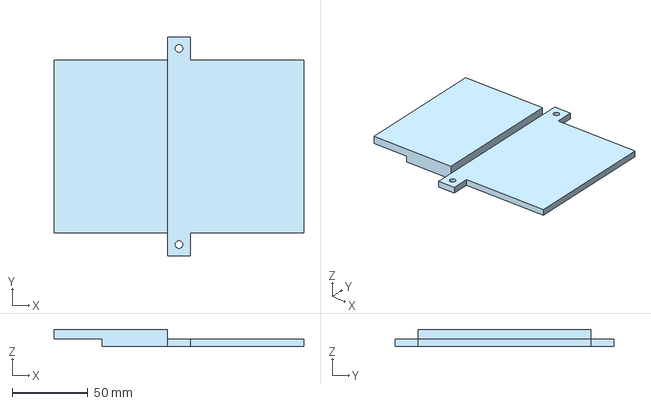
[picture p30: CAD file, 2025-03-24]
system_development/Keowee/V0.2.1/Solar_Panel/3D Prints/battery case lid.3mf
165.1 x 144.8 x 11.4 mm

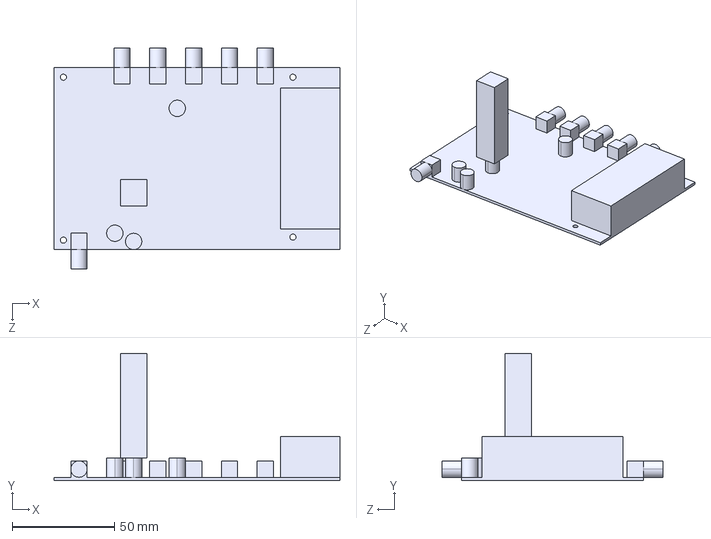
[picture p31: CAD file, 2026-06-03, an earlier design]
system_development/Moultrie/v0.3.1/CAD/NMR_Mainboard.STEP
139.7 x 62.1 x 108.0 mm

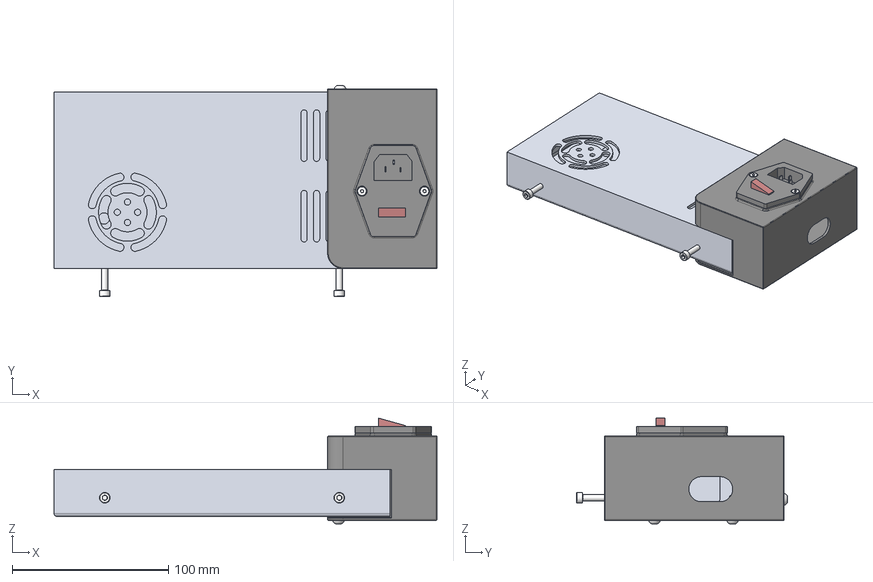
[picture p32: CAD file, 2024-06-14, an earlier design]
system_development/Moultrie/v0.1.0/CAD/PSU dependencies/Ender 3 PSU.step
245.0 x 135.2 x 67.7 mm
24V15A power supply_Standard
power switch_Standard
Power holder_Standard
M3X10 Flush Head Screw_Standard x 2
M4X20 Socket Head Screw_Standard x 2
M4X16 Pan Head Screw_Standard x 3

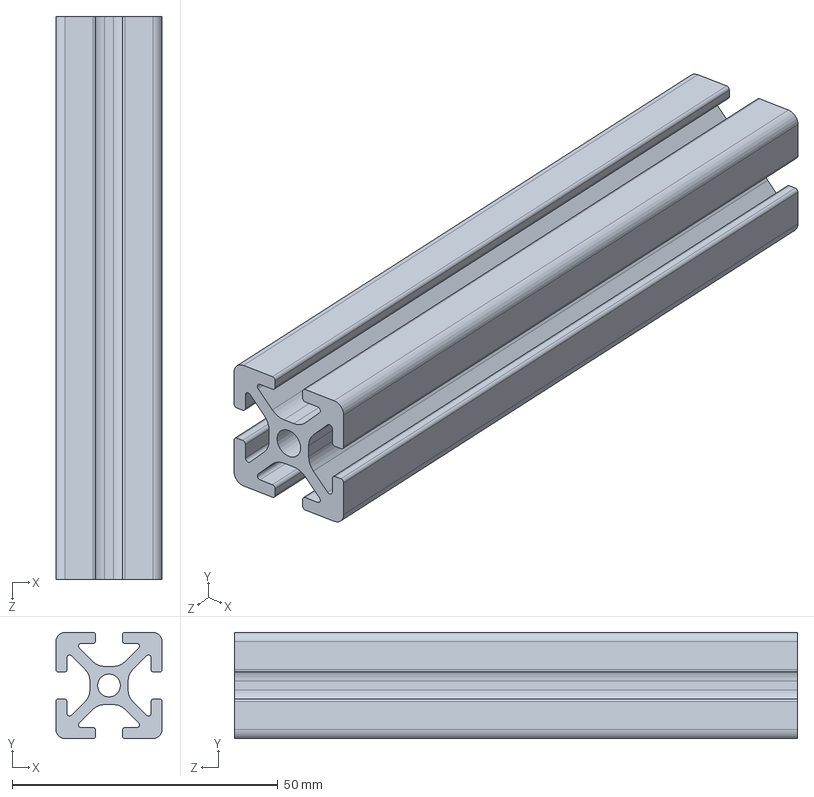
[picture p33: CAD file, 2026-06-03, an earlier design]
system_development/Moultrie/v0.3.0/CAD/AL106.SLDPRT
20.0 x 20.0 x 106.0 mm

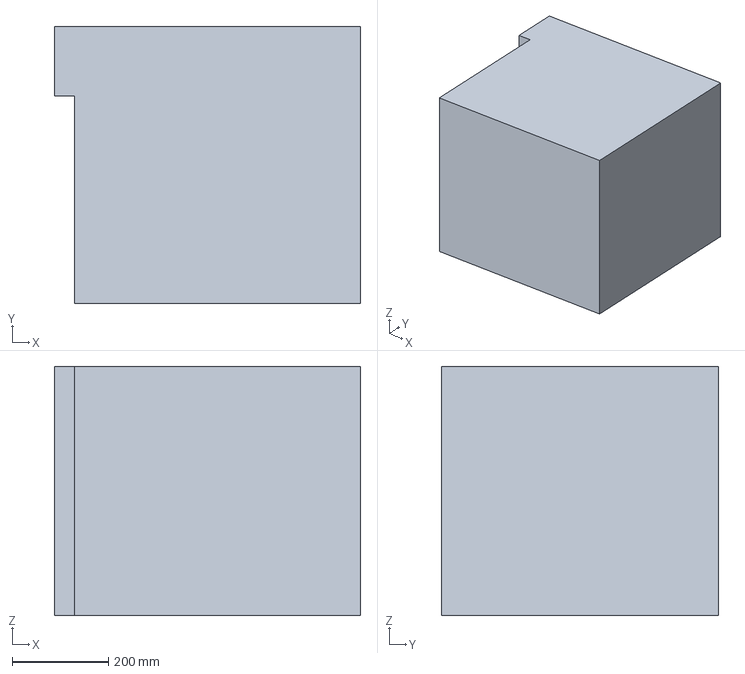
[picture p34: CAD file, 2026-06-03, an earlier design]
system_development/Moultrie/v0.3.0/CAD/Frame/[updated] Medium IncuFridge 365P v11.step
635.0 x 574.7 x 517.5 mm

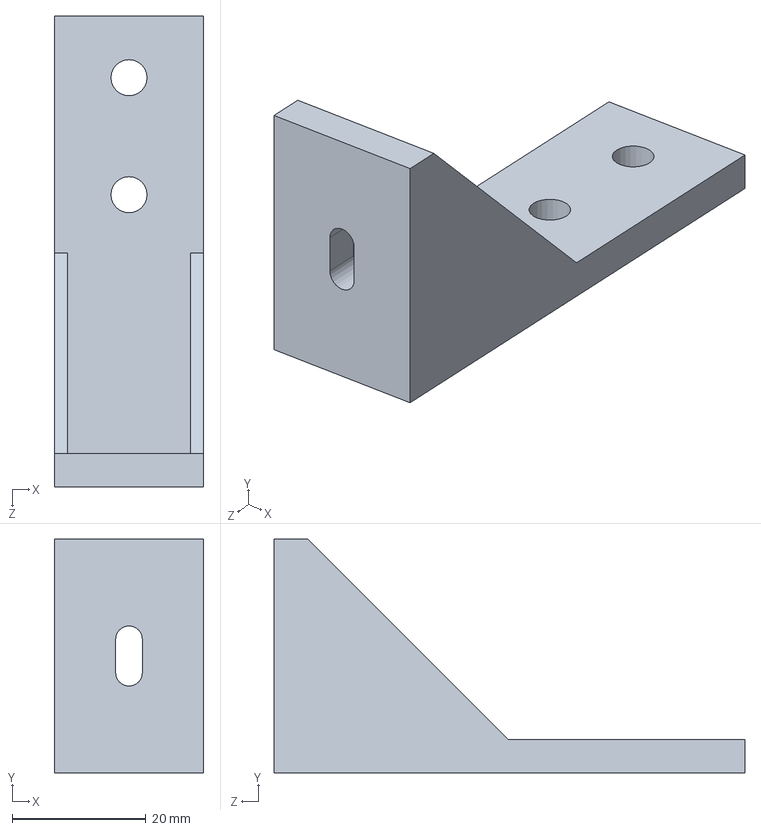
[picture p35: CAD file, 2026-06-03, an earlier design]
system_development/Moultrie/v0.3.1/CAD/DAQBracket.25.SLDPRT
22.4 x 35.0 x 70.4 mm

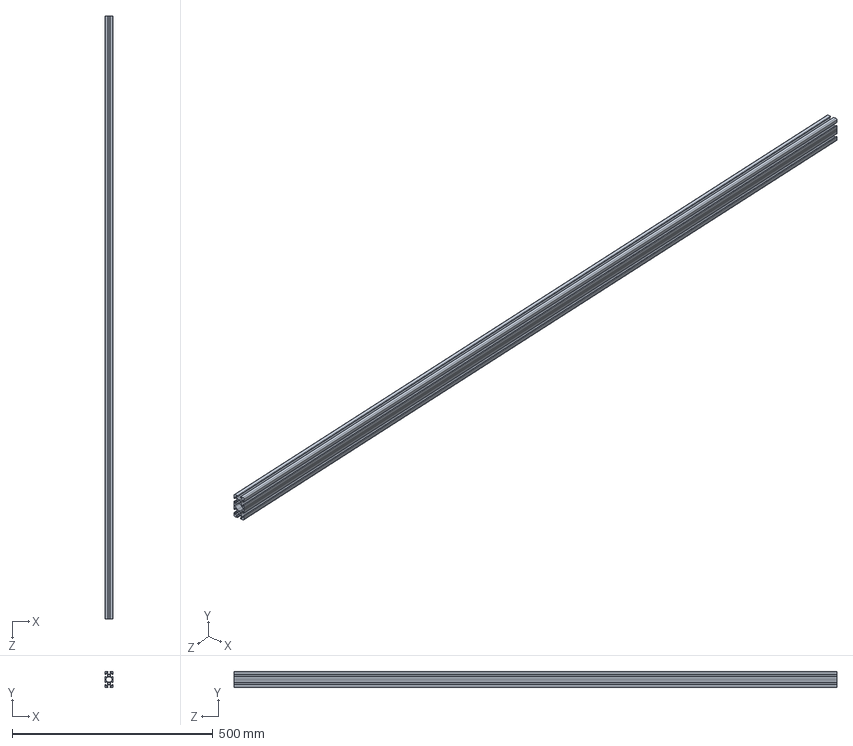
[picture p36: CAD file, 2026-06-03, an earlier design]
system_development/Moultrie/v0.3.1/CAD/Frame/40x20ExtrudedAl 150cm.SLDPRT
20.0 x 40.0 x 1500.0 mm

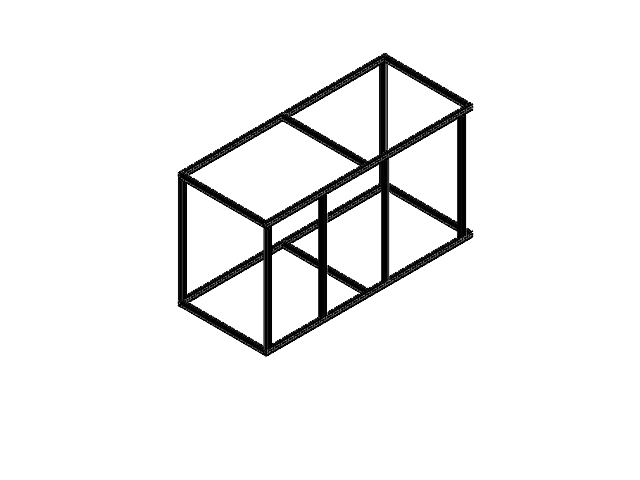
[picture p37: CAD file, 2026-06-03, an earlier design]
system_development/Moultrie/v0.3.0/CAD/Frame/Frame.SLDASM
40x20ExtrudedAl 150cm x 4
40x20ExtrudedAl 76cm x 6
40x20ExtrudedAl 60cm x 6

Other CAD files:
system_development/Moultrie/v0.4.2/NMRtray/Al Bars/20x40.dwg
system_development/Moultrie/v0.4.1/NMRtray/Al Bars/20x40.dwg
system_development/Moultrie/v0.3.0/CAD/DAQBracketv3.STL
system_development/Moultrie/v0.1.0/CAD/10.425in T-Slot.ipt
system_development/Moultrie/v0.1.0/CAD/12.95in T-Slot.ipt
system_development/Moultrie/v0.1.0/CAD/12in T-Slot.ipt
system_development/Moultrie/v0.1.0/CAD/18.4in T-Slot.ipt
system_development/Moultrie/v0.1.0/CAD/2.25in T-Slot.ipt
system_development/Moultrie/v0.1.0/CAD/5 in T-Slot.ipt
system_development/Moultrie/v0.1.0/CAD/Ender 3 PSU.iam
system_development/Moultrie/v0.1.0/CAD/Full Assembly.iam
system_development/Moultrie/v0.1.0/CAD/Magnet.ipt
system_development/Moultrie/v0.1.0/CAD/OldVersions/10.425in T-Slot.0006.ipt
system_development/Moultrie/v0.1.0/CAD/OldVersions/12.95in T-Slot.0006.ipt
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

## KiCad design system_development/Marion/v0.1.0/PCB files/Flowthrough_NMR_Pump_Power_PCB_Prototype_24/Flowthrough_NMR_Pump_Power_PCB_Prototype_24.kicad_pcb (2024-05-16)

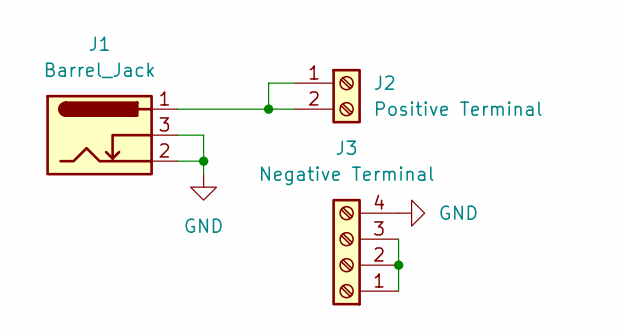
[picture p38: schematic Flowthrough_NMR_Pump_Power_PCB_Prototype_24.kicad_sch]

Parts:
J1: Barrel_Jack; BarrelJack_Horizontal
J2: Positive Terminal; TerminalBlock_Phoenix_MKDS-1,5-2-5.08_1x02_P5.08mm_Horizont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
J3: Negative Terminal; TerminalBlock_Phoenix_MKDS-1,5-4-5.08_1x04_P5.08mm_Horizont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

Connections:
GND: J1.2, J1.3, J3.4
unnamed: J1.1, J2.1, J2.2
unnamed: J3.1, J3.2, J3.3

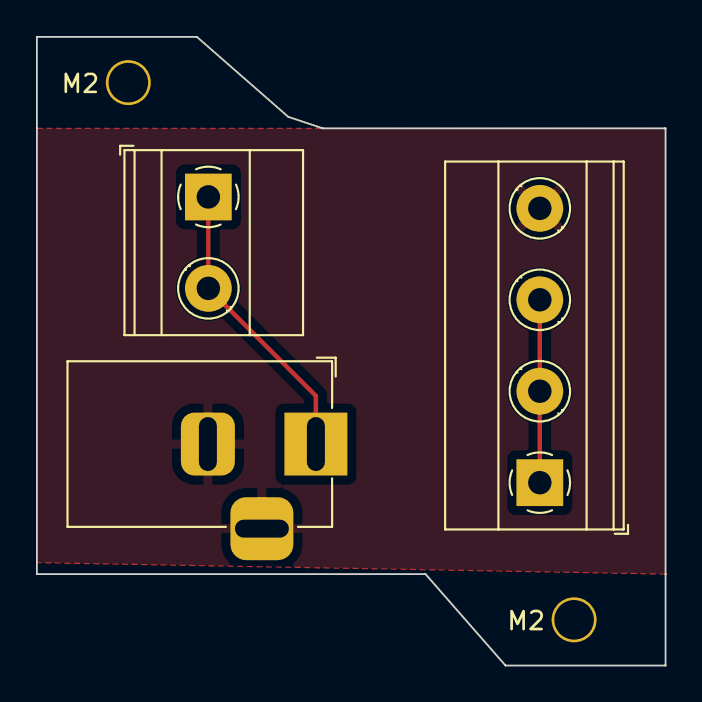
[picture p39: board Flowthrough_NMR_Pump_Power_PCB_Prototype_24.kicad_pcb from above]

Board: 2 copper layers, 34.9 x 34.9 mm, 3 parts (0 on the bottom side), 3 nets.

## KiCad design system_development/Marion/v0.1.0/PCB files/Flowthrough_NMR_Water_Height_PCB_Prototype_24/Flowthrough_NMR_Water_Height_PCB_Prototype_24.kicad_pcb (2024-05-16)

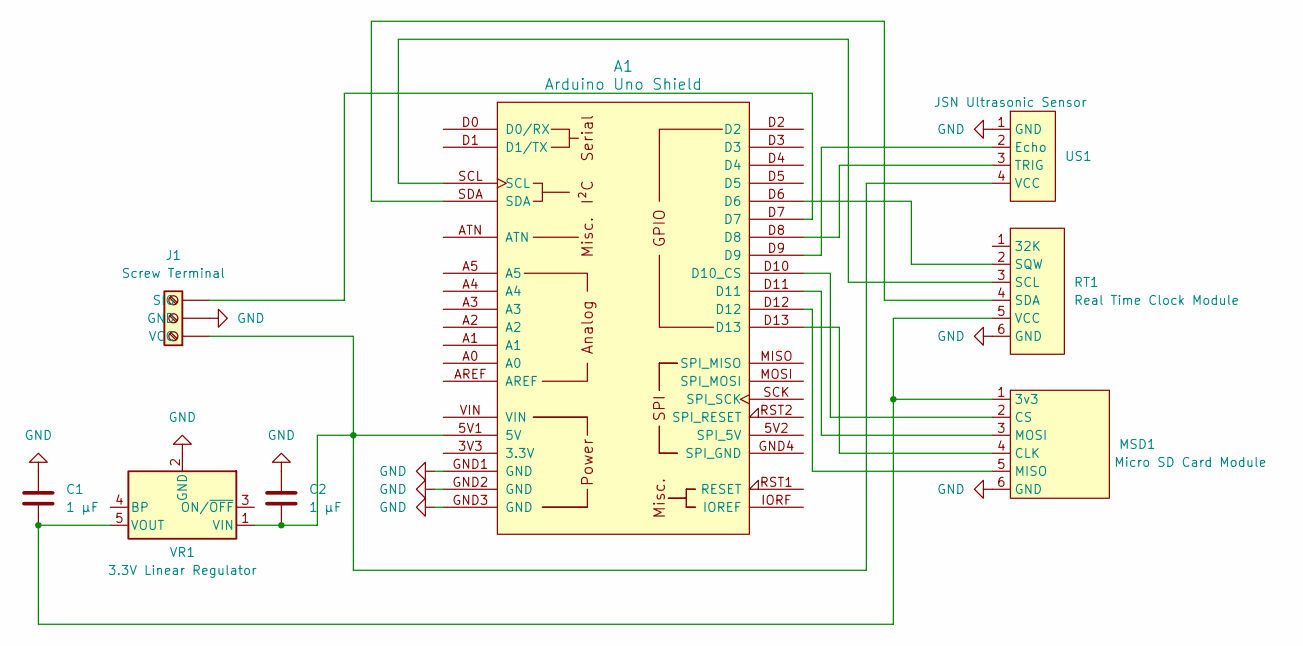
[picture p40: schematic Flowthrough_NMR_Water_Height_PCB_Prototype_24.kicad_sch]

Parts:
A1: Arduino Uno Shield; Arduino_101_Shield
C1, C2: 1 μF; C_1206_3216Metric
J1: Screw Terminal; TerminalBlock_Phoenix_MKDS-1,5-3-5.08_1x03_P5.08mm_Horizont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
MSD1: Micro SD Card Module; PinSocket_1x06_P2.54mm_Vertical
RT1: Real Time Clock Module; PinSocket_1x06_P2.54mm_Vertical
US1: JSN Ultrasonic Sensor; PinSocket_1x04_P2.54mm_Vertical
VR1: 3.3V Linear Regulator; SOT-23-5

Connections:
GND: A1.GND1 (GND), A1.GND2 (GND), A1.GND3 (GND), C1.1, C2.1, J1.2 (GND), MSD1.6 (GND), RT1.6 (GND), US1.1 (GND), VR1.2 (GND)
unnamed: A1.5V1 (5V), C2.2, J1.1 (VCC), US1.4 (VCC), VR1.1 (VIN)
unnamed: A1.D10 (D10_CS), MSD1.2 (CS)
unnamed: A1.D7, J1.3 (SIG)
unnamed: C1.2, MSD1.1 (3v3), RT1.5 (VCC), VR1.5 (VOUT)
unnamed: A1.D13, MSD1.4 (CLK)
unnamed: A1.D12, MSD1.5 (MISO)
unnamed: A1.D11, MSD1.3 (MOSI)
unnamed: A1.SCL, RT1.3 (SCL)
unnamed: A1.SDA, RT1.4 (SDA)
unnamed: A1.D6, RT1.2 (SQW)
unnamed: A1.D9, US1.2 (Echo)
unnamed: A1.D8, US1.3 (TRIG)

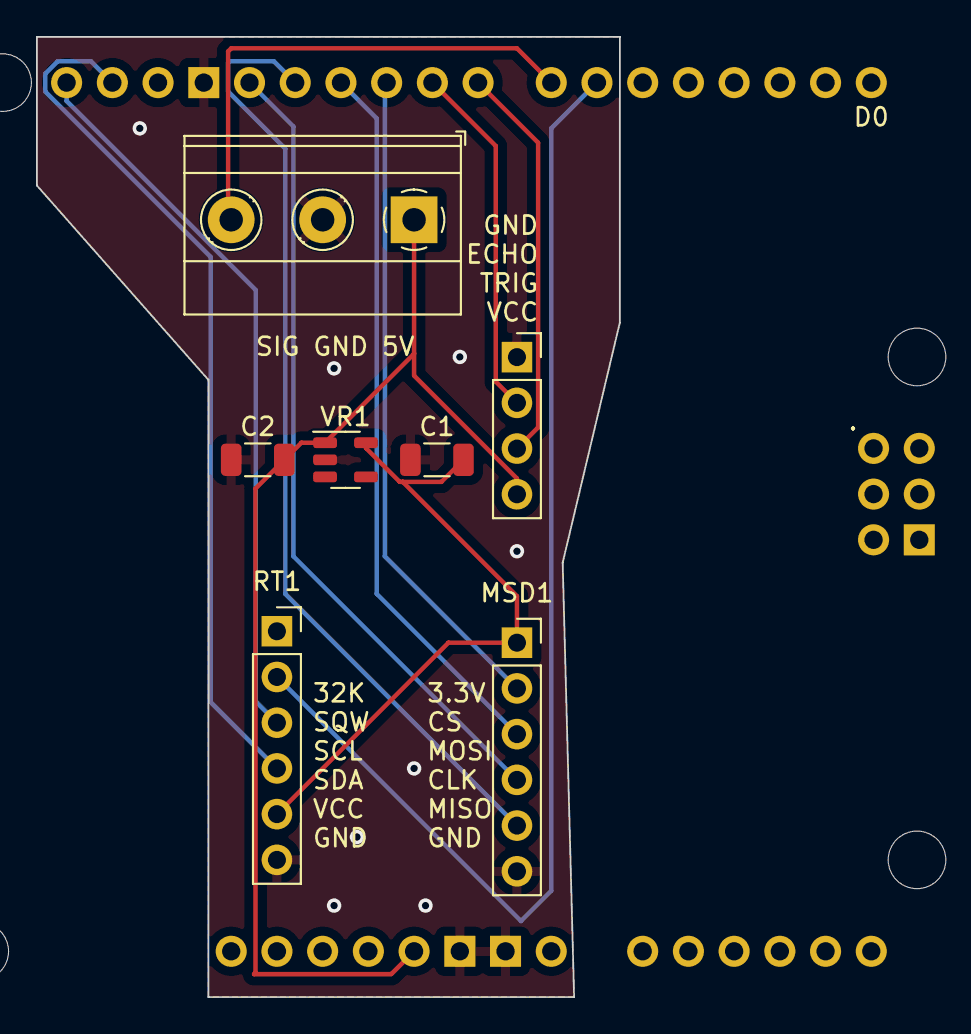
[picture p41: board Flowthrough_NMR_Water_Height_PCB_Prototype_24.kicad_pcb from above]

Board: 2 copper layers, 32.4 x 53.3 mm, 8 parts (0 on the bottom side), 13 nets.

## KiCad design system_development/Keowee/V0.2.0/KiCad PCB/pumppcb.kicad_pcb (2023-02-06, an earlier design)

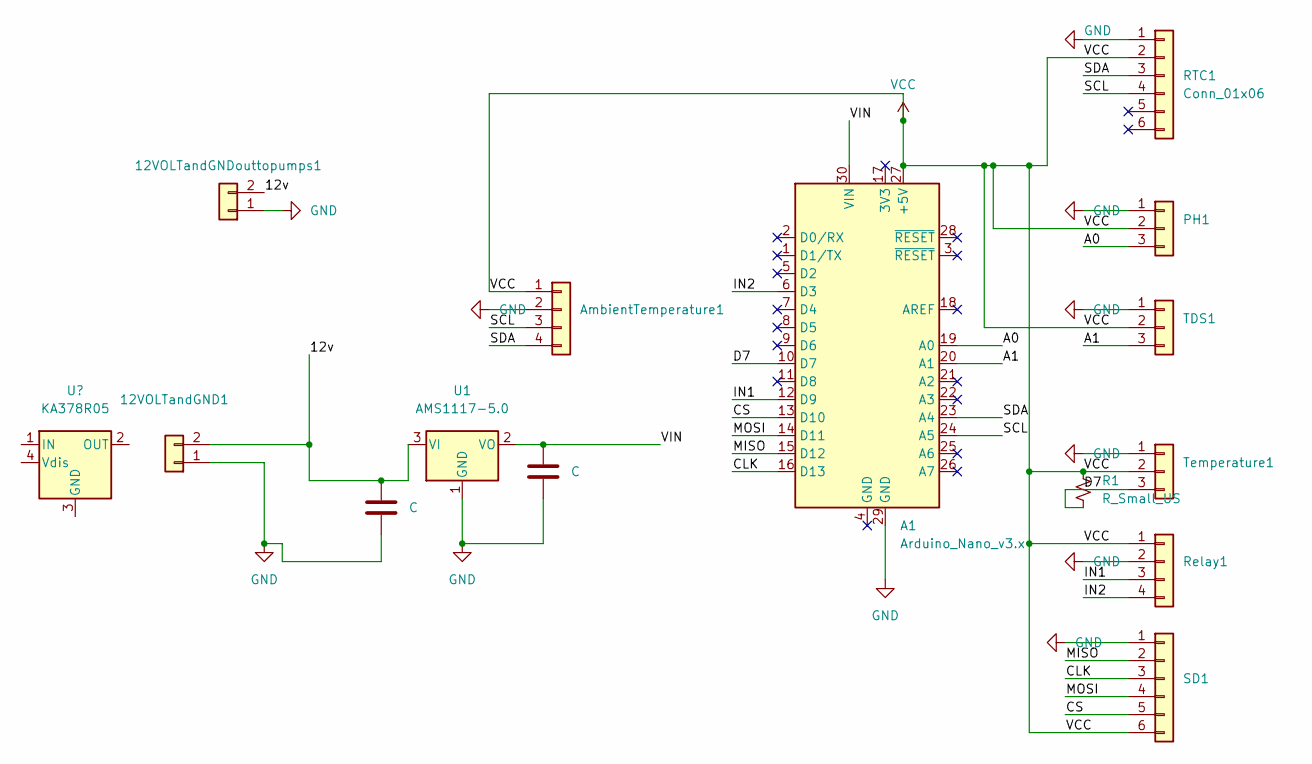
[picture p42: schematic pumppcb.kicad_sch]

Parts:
12VOLTandGND1, 12VOLTandGNDouttopumps1: Conn_01x02; PinHeader_1x02_P2.54mm_Vertical
A1: Arduino_Nano_v3.x; Arduino_Nano
AmbientTemperature1: Conn_01x04; PinHeader_1x04_P2.54mm_Vertical
C1, C2: C; CP_Elec_4x5.8
PH1: Conn_01x03; PinHeader_1x03_P2.54mm_Vertical
R1: R_Small_US; R_Axial_DIN0309_L9.0mm_D3.2mm_P2.54mm_Vertical
RTC1: Conn_01x06; PinHeader_1x06_P2.54mm_Vertical
Relay1: Conn_01x04; PinHeader_1x04_P2.54mm_Vertical
SD1: Conn_01x06; PinHeader_1x06_P2.54mm_Vertical
TDS1: Conn_01x03; PinHeader_1x03_P2.54mm_Vertical
Temperature1: Conn_01x03; PinHeader_1x03_P2.54mm_Vertical
U1: AMS1117-5.0; SOT-223-3_TabPin2

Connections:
/12v: 12VOLTandGND1.2, 12VOLTandGNDouttopumps1.2, C1.2, U1.3 (VI); also elsewhere on the board
/A0: A1.19 (A0), PH1.3
/A1: A1.20 (A1), TDS1.3
/CLK: A1.16 (D13), SD1.3
/CS: A1.13 (D10), SD1.5
/D7: A1.10 (D7), R1.2, Temperature1.3
/IN1: A1.12 (D9), Relay1.3
/IN2: A1.6 (D3), Relay1.4
/MISO: A1.15 (D12), SD1.2
/MOSI: A1.14 (D11), SD1.4
/SCL: A1.24 (A5), AmbientTemperature1.3, RTC1.4
/SDA: A1.23 (A4), AmbientTemperature1.4, RTC1.3
/VIN: A1.30 (VIN), C2.2, U1.2 (VO)
GND: 12VOLTandGND1.1, 12VOLTandGNDouttopumps1.1, A1.29 (GND), AmbientTemperature1.2, C1.1, C2.1, PH1.1, RTC1.1, Relay1.2, SD1.1, TDS1.1, Temperature1.1, U1.1 (GND); also elsewhere on the board
VCC: A1.27 (+5V), AmbientTemperature1.1, PH1.2, R1.1, RTC1.2, Relay1.1, SD1.6, TDS1.2, Temperature1.2

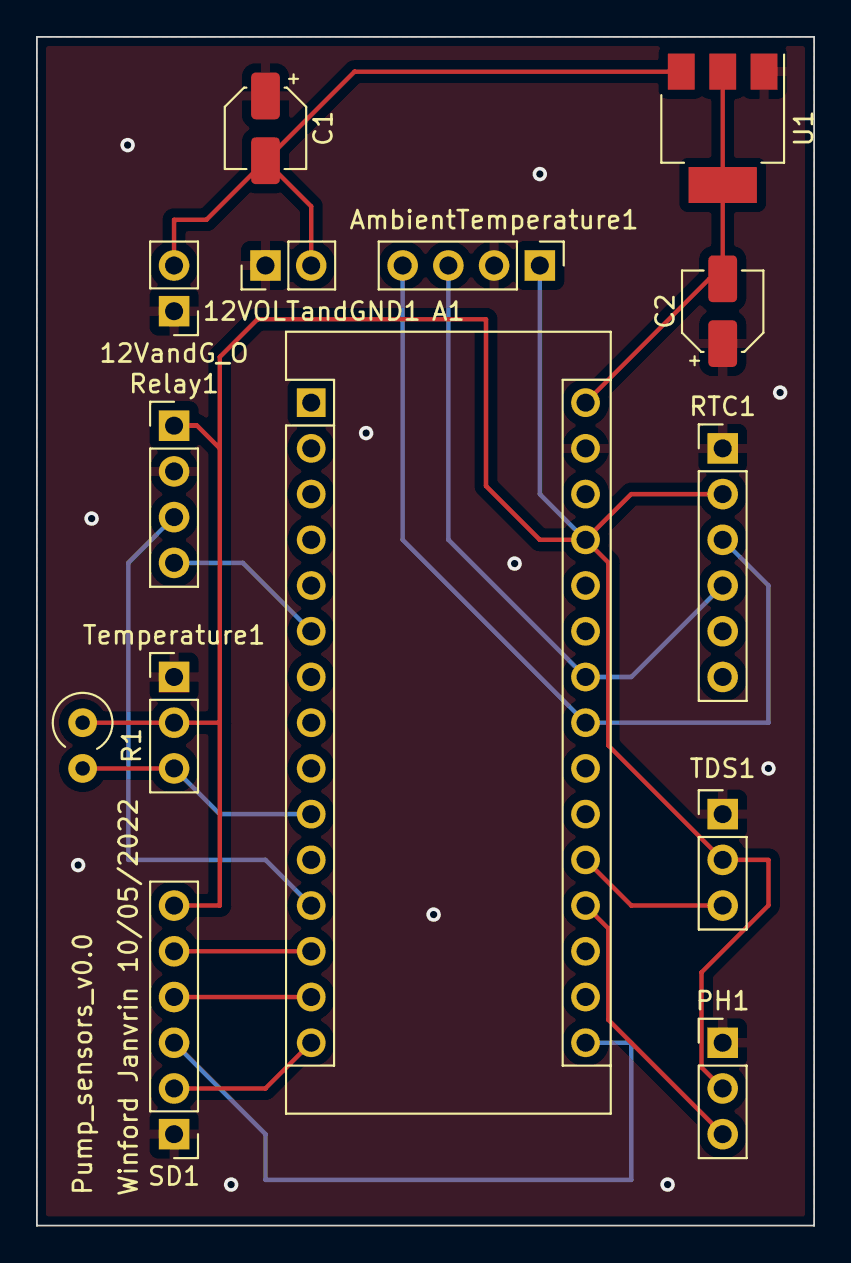
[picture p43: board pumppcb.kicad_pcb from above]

Board: 2 copper layers, 43.2 x 66.0 mm, 14 parts (0 on the bottom side), 15 nets.

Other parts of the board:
12VandG_O: Conn_01x02; PinHeader_1x02_P2.54mm_Vertical

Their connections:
/12v: 12VandG_O.2; also elsewhere on the board
GND: 12VandG_O.1; also elsewhere on the board

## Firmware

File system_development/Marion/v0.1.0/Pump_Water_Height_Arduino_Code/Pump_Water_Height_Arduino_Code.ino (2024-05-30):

//Water Height Sensor developed by Nicholas Liger, from previous work by Corrine Smith and Winford Janvrin
//in conjuction with ARTS - LAB at University of South and Carolina for the flowthrough NMR project

#include <SPI.h>  //SPI communication library
#include <SD.h> //SD card library
#include <Wire.h> //Wire library for communicating with I2C and the RTC
#include <DS3231.h> //library for RTC module
#include <LowPower.h>
#include "NewPing.h" //New Ping library for use with the sonar sensors

const int trigPin1 = 0; //trigger pin for sonar sensor 1
const int echoPin1 = 0; //echo pin for sonar sensor 1
const int maxDist = 450; // max distance for sonar sensor, same for both
NewPing sonar_sensor_1(trigPin1, echoPin1, maxDist); //set up NewPing variable for sonar sensor 1
float distance1=0; //variable for distance measured by sonar sensor 1 used to publish to Adafruit IO via MQTT 
float origDist1=0; //Original distance for sensor 1 that is used to calibrate the height measurement of the water
float origHeight1 = 0; //Height of the water beneath sensor 1, measured at the time of installation
float height1 = 0; //Height variable for the current water height calculated from distance1

//Variables for setting up the SD card and RTC
char timeStamp[32]; //Char/string variable for holding time stamp
const int chipSelect = 53; //Chip Select for the SD card
char dayStampFileName[20]; //Char/string variable for holding the day stamp for naming
//file in SD card
RTClib myRTC; //RTC variable for using DS3231 library scripts
uint8_t currentTime = 1;
uint8_t lastTime = 1;

void setup() {
  // put your setup code here, to run once:
  Serial.begin(9600); //begin the Serial monitor
  Wire.begin(); //begin communication with I2C, needed for RTC module
  Serial.print("Initializing SD card...");

  // see if the card is present and can be initialized:
  if (!SD.begin(chipSelect)) {
    Serial.println("Card failed, or not present");
    // don't do anything more:
    while (1);
  }
  Serial.println("card initialized.");
  origDist1 = sonar_sensor_1.ping_cm();
}

void loop() {
  // put your main code here, to run repeatedly:
  DateTime now = myRTC.now();  
  currentTime = now.minute();
  if (currentTime %5 == 0 && currentTime != lastTime ){
    //This section creates the timestamps from the RTC module
    sprintf(timeStamp, "%02d:%02d:%02d %02d/%02d/%02d", now.hour(), now.minute(), now.second(), now.day(), now.month(), now.year());  
    snprintf(dayStampFileName, 20, "%02d%02d%02d.txt", now.day(), now.month(), now.year());  
    Serial.print(F("Date/Time: "));
    Serial.println(timeStamp);
    distance1 = sonar_sensor_1.ping_cm();
    height1 = origHeight1 + (origDist1 - distance1)/(2.54*12);
    // This section saves the data to the SD card
    Serial.println(dayStampFileName);
    //This line creates a new file named with the day time stamp (DDMMYYYY)
    //or opens the file if this name already exists
    //The SD cards have a tendency to become corrupted which can ruin a long term test
    //if the data is all saved to a single file, so this method creates a new CSV for every day
    //so that even if a file is corrupted, we will still have the data from every other day
    if (SD.exists(dayStampFileName) == 0) {
      File dataFile = SD.open(dayStampFileName, FILE_WRITE);
      if (dataFile){
        dataFile.println("Ultrasonic 1 Height Reading (ft), Timestamp");
        dataFile.close();
      }
      else {
      Serial.println("error opening datalog.txt");
      }
    }
    File dataFile = SD.open(dayStampFileName, FILE_WRITE);
    if (dataFile) {
        dataFile.print(height1);
        dataFile.print(",");
        dataFile.println(timeStamp);
        dataFile.close();
      }
    // if the file isn't open, pop up an error:
    else {
      Serial.println("error opening datalog.txt");
    }
  }
  else {
  LowPower.powerDown(SLEEP_8S, ADC_OFF, BOD_OFF); 
  }
}

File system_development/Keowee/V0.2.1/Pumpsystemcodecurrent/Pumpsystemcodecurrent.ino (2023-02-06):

#include <OneWire.h> 
#include <DallasTemperature.h>
#include <SPI.h>
#include <SD.h>
#include <EEPROM.h>
#include <GravityTDS.h>
#include <Wire.h>
#include <Adafruit_Sensor.h>
#define TdsSensorPin A1
#include <DS323x.h>
#define SEALEVELPRESSURE_HPA (1013.25)
#ifdef USE_PULSE_OUT
  #include "ph_iso_grav.h"       
  Gravity_pH_Isolated pH = Gravity_pH_Isolated(A0);         
#else
  #include "ph_grav.h"             
  Gravity_pH pH = Gravity_pH(A0);   
#endif
                

uint8_t user_bytes_received = 0;                
const uint8_t bufferlen = 32;                   
char user_data[bufferlen];                     

void parse_cmd(char* string) {                   
  strupr(string);                                
}                   


DS323x rtc;
GravityTDS gravityTds;
const int chipSelect = 10;
float temperature = 25, tdsValue = 0;
File myFile;
void save_temperature() {}

const int SENSOR_PIN = 7; 

OneWire oneWire(SENSOR_PIN);         
DallasTemperature tempSensor(&oneWire); 

float tempCelsius;  


void setup() 
{
  
  Serial.begin(115200);
  pinMode(9,OUTPUT);
  pinMode(3,OUTPUT);
  
  tempSensor.begin();
  gravityTds.setPin(TdsSensorPin);
  gravityTds.setAref(5.0);  //reference voltage on ADC, default 5.0V on Arduino UNO
  gravityTds.setAdcRange(1024);  //1024 for 10bit ADC;4096 for 12bit ADC
  gravityTds.begin();  //initialization
   
  
  Wire.begin();
   rtc.attach(Wire);
   rtc.now(DateTime(2022, 10, 7, 12, 45,0));

  if (!SD.begin(chipSelect)) {
    while (true);
  }
 
}

void loop() {
 
  digitalWrite(9,HIGH);
  digitalWrite(3,HIGH);

  delay(60000);

  digitalWrite(9,LOW);
  digitalWrite(3,LOW);

  delay(1000);
    
  tempSensor.requestTemperatures();             // send the command to get temperatures
  tempCelsius = tempSensor.getTempCByIndex(0);  // read temperature in Celsius
  
  gravityTds.setTemperature(temperature);  // set the temperature and execute temperature compensation
  gravityTds.update();  //sample and calculate
  tdsValue = gravityTds.getTdsValue();  // then get the value

  if (Serial.available() > 0) {                                                      
    user_bytes_received = Serial.readBytesUntil(13, user_data, sizeof(user_data));   
  }

  if (user_bytes_received) {                                                      
    parse_cmd(user_data);                                                          
    user_bytes_received = 0;                                                        
    memset(user_data, 0, sizeof(user_data));                                         
  }

  
  
  
  DateTime now = rtc.now();
  Serial.println(now.timestamp());
  
  File dataFile = SD.open("sheriff.csv", FILE_WRITE);
  if (dataFile) {
    dataFile.print(tdsValue, 0);
    dataFile.print(",");
    dataFile.print(" ");
    dataFile.print("ppm");
    dataFile.print(",");
    dataFile.print(" ");
    dataFile.print(pH.read_ph());
    dataFile.print(",");
    dataFile.print(" ");
    dataFile.print(tempCelsius);
    dataFile.print(",");
    dataFile.print(" ");
    dataFile.print("°C");
    dataFile.print(",");
    dataFile.print(" ");
    dataFile.println(now.timestamp());
    
    dataFile.close();
  }


 delay(240000);
  
}

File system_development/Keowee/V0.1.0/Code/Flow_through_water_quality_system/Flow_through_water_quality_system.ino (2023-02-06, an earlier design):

#include <OneWire.h>
#include <DallasTemperature.h>
#include <SPI.h>
#include <SD.h>
#include <EEPROM.h>
#include <GravityTDS.h>
#include <Wire.h>
#include <Adafruit_Sensor.h>
#include <Adafruit_BME280.h>
#define TdsSensorPin A1
#include <DS323x.h>
#define SEALEVELPRESSURE_HPA (1013.25)

#ifdef USE_PULSE_OUT
  #include "ph_iso_grav.h"       
  Gravity_pH_Isolated pH = Gravity_pH_Isolated(A0);         
#else
  #include "ph_grav.h"             
  Gravity_pH pH = Gravity_pH(A0);   
#endif
                

uint8_t user_bytes_received = 0;                
const uint8_t bufferlen = 32;                   
char user_data[bufferlen];                     

void parse_cmd(char* string) {                   
  strupr(string);                                
}                   

Adafruit_BME280 bme;
DS323x rtc;
GravityTDS gravityTds;

const int chipSelect = 10;
float temperature = 25, tdsValue = 0;
File myFile;
void save_temperature() {}

const int SENSOR_PIN = 7; 

OneWire oneWire(SENSOR_PIN);         
DallasTemperature tempSensor(&oneWire); 

float tempCelsius;    
float tempFahrenheit; 


void setup() 
{
  
  Serial.begin(115200);
  pinMode(9,OUTPUT);
  pinMode(3,OUTPUT);
  
  tempSensor.begin();
  gravityTds.setPin(TdsSensorPin);
  gravityTds.setAref(5.0);  //reference voltage on ADC, default 5.0V on Arduino UNO
  gravityTds.setAdcRange(1024);  //1024 for 10bit ADC;4096 for 12bit ADC
  gravityTds.begin();  //initialization
   
  
  Wire.begin();
  if (pH.begin()) {                                     
    Serial.println("Loaded EEPROM");
  }
   rtc.attach(Wire);
   rtc.now(DateTime(2022, 2, 2, 6, 42,0));
  Wire.begin();
  if (!bme.begin(0x76)) {
    Serial.println("Could not find a valid BME280 sensor, check wiring!");
    while (1);
  }
   while (!Serial);

  Serial.print("Initializing SD card...");

  if (!SD.begin(chipSelect)) {
    Serial.println("initialization failed. Things to check:");
    while (true);
  }

  Serial.println("initialization done.");
  
 
}

void loop() {
 
  digitalWrite(9,HIGH);
  digitalWrite(3,HIGH);
  
  
  tempSensor.requestTemperatures();             // send the command to get temperatures
  tempCelsius = tempSensor.getTempCByIndex(0);  // read temperature in Celsius
  tempFahrenheit = tempCelsius * 9 / 5 + 32; // convert Celsius to Fahrenheit
  
  gravityTds.setTemperature(temperature);  // set the temperature and execute temperature compensation
  gravityTds.update();  //sample and calculate
  tdsValue = gravityTds.getTdsValue();  // then get the value

  if (Serial.available() > 0) {                                                      
    user_bytes_received = Serial.readBytesUntil(13, user_data, sizeof(user_data));   
  }

  if (user_bytes_received) {                                                      
    parse_cmd(user_data);                                                          
    user_bytes_received = 0;                                                        
    memset(user_data, 0, sizeof(user_data));                                         
  }

  
  
  Serial.print(tdsValue, 0);
  Serial.print("ppm");
  Serial.print(",");
  Serial.print(" ");
  Serial.print(pH.read_ph());
  Serial.print("ph ");
  Serial.print(",");
  Serial.print(" ");
  Serial.print(" Ambient Temp = ");
  Serial.print(bme.readTemperature());
  Serial.println("*C");
  Serial.print(",");
  Serial.print(" ");
  Serial.print("Temperature: ");
  Serial.print(tempCelsius);    // print the temperature in Celsius
  Serial.print("°C");
  Serial.print(",");
  Serial.print(" ");        // separator between Celsius and Fahrenheit
  DateTime now = rtc.now();
  Serial.println(now.timestamp());
  
  File dataFile = SD.open("sheriff.csv", FILE_WRITE);
  if (dataFile) {
    dataFile.print(tdsValue, 0);
    dataFile.print("ppm");
    dataFile.print(",");
    dataFile.print(" ");
    dataFile.print(pH.read_ph());
    dataFile.print(",");
    dataFile.print(" ");
    dataFile.print(tempCelsius);
    dataFile.print("°C");
    dataFile.print(",");
    dataFile.print(" ");
    dataFile.print(" Ambient Temp = ");
    dataFile.print(bme.readTemperature());
    dataFile.print("*C");
    dataFile.print(",");
    dataFile.print(" ");
    dataFile.println(now.timestamp());
    
    dataFile.close();
  }
  else {
    Serial.println("error opening datalog.txt");
  }

 delay(5000);
  
}

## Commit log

2022-09-15 Flow through water quality system Arduino code
2022-10-03 Create Pumpsystemcodeoctober.ino
    Same as 0.1 except pump runs for 60 seconds takes measurements then turns off for 5 minutes.
2024-05-12 initial push of re-vamped repo
    [pumppcb.kicad_pcb, pumppcb.kicad_sch]
2024-05-12 Added front page readme
    [pumppcb.kicad_pcb, pumppcb.kicad_sch]
2024-05-16 Created PCB's for Water Height Monitoring
    [Pump Power PCB.kicad_pcb, Pump Power PCB.kicad_sch, Water Height and Flowthrough PCB.kicad_pcb, Water Height and Flowthrough PCB.kicad_sch]
2024-05-16 Altered PCB's
    [Pump Power PCB.kicad_pcb]
2024-05-16 added parts list
    [PCB Parts List.csv]
2024-05-17 Create ~Water Height and Flowthrough PCB.kicad_pcb.lck
2024-06-14 Renamed Prototype to Marion
    [Flowthrough_NMR_Pump_Power_PCB_Prototype_24.kicad_pcb, Flowthrough_NMR_Pump_Power_PCB_Prototype_24.kicad_sch, Flowthrough_NMR_Water_Height_PCB_Prototype_24.kic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]
2024-06-14 Updated Rough CAD
    for now this mostly serves to make sure we have the dimensions right before we build. It'll look nicer later
    [10.425in T-Slot.0006.ipt, 10.425in T-Slot.ipt, 12.95in T-Slot.0006.ipt, 12.95in T-Slot.ipt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]
2024-07-23 Updated sensor array
2024-07-23 Current Code for the sensor array and pump
2024-07-23 current code for the testing kit
2025-01-21 Create Flowthrough_NMR_labVIEW
2025-03-24 added solar panel prints
    [battery case holder.3mf, battery case lid.3mf, power output frame.3mf, power output lid.3mf]
2025-09-22 added v 0.2.1
    [BOM-flow-through-V0.2.1.xlsx, battery case holder.3mf, battery case lid.3mf, power output frame.3mf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]
2025-09-26 added cart folder
    [BOM-v0.3-cart.xlsx]
2025-10-14 Update BOM-v0.3-cart.xlsx
    Added all supplies to BOM
    [BOM-v0.3-cart.xlsx]
2026-06-03 New CAD files added
    [40x20ExtrudedAl 150cm.SLDPRT, 40x20ExtrudedAl 60cm.SLDPRT, 40x20ExtrudedAl 76cm.SLDPRT, 40x20ExtrudedAl.SLDPRT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]
2026-06-08 BOM updated
    [BOM-v0.3-cart.xlsx]
2026-06-08 Updated BOM
    [BOM-v0.3-cart.xlsx]
